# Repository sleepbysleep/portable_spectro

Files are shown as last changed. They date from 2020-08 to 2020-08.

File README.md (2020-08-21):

# Introduction
I just want to make new kind of portable spectrometer, which would be equipped with more-efficient LED illumination ranging from 400nm to 1000nm than Tungsten-Hallogen lamp. The design intends to be switchable between two kinds of miniatured spectrometer(i.e. C12880MA, and ADS8860IDGS) for flexiblity. Indeed, the main controller should handle BlueTooth communication with intermediate device like smart phone or personal computer in order to gather the spectrum data into remote server.

In terms of Vis/NIR radiation, the useful choices are so-called braodband IR LED like SFH4736, SFH4776, and L1IG-0750100000000. Unfortunately, these things doesn't emit visible light except for violet band, which intends to make a phosper excited. So, I have to make the lighting in the combination of Vis LED and such a broadband LEDs. To accomplish proper illumination, many things have to be solved in aspects of blending ratio of Vis, and NIR, and how many LEDs are mounted on PCB for sufficient lighting. Therefore, the below have to be done;

1. Analyze the comparision of spectral intensity among SFH4736, SFH4776, and L1IG-0750100000000.
2. Determine blending ratio of Vis, and NIR LEDs for flatness of spectral intensity from Vis to NIR.
3. Design the hardware that can equip with nRF52840, Vis/NIR LEDs (corresponding driver as well), switchable spectrometer (corresponding periphertal indeed), and power management unit including Li-ion or Li-po battery, charging part, and boost regulator.
4. Develop the firmware that can process the BlueTooth communication with smart phone (iOS, and Android), interfacing the spectrometer, and interactive operation between LED-based illumination, and spectrometer.
5. Develop the application for iOS, and Android that can be portal to pass, and signal process the spectrum into the remote server.
6. Develop the remote server program, that can manage huge spectra with extra infomation (i.e. object, date, dependant like sugar content), and do machine learning, initially being PLS, and SVM-regression hopefully I want to goes into Deap Learning (CNN or RNN).

Definitly, all the staffs are very challenging to me in terms of funding, and workloads. I will do as much as possible!

# Hardware
The hardware consists of Li-ion or Li-po battery, charging unit, boost regulator, C12880MA spectrometer including analog amplifier, and ADC unit, AS7260X spectrometer, and nRF52840 BlueTooth CPU.

TODO: Block diagram

The schematic of ADS8860IDGS is referred from https://www.ti.com/lit/df/tidrau9a/tidrau9a.pdf
TODO: add image with highlight of the copied.

The schematic of C12880MA is referred from https://github.com/Alexey-Danilchenko/Spectron
TODO: add image with highlight of the copied

The schematic of AS7260x is referred from

The schematic of MCP73871 is referred from 

# Mechanical Drawing

# Spectral intesity comparison
TODO: add the graph among them.

# Firmware Design
openocd, my budget is the stlink v2
TODO: add Flow chart
TODO: add block diagram

# Integration time calculation

# App Design

# Server Design

# BOM
Spectrometer: C12880MA, or AS7260x be switchable
CPU: nrf52840, mdbt501-v10
Candidators for Light source: SFH4736, or SFH4776, or L1IG-0750100000000

# References
https://github.com/Alexey-Danilchenko/Spectron

# Appendix

## nRF52840 development environment

Install Toolchain on debian testing(currently bulleseye)
$ apt install libnewlib-dev libstdc++-arm-none-eabi-newlib libnewlib-arm-none-eabi gcc-arm-none-eabi binutils-arm-none-eabi

Verify the version of installed gcc
$ arm-none-eabi-gcc --version
arm-none-eabi-gcc (15:7-2018-q2-6+b1) 7.3.1 20180622 (release) [ARM/embedded-7-branch revision 261907]
Copyright (C) 2017 Free Software Foundation, Inc.
This is free software; see the source for copying conditions.  There is NO
warranty; not even for MERCHANTABILITY or FITNESS FOR A PARTICULAR PURPOSE.

Download, and install the nRF5 SDK
Go to https://www.nordicsemi.com/Software-and-Tools/Software/nRF5-SDK/, and
download the latest verion of SDK at https://www.nordicsemi.com/-/media/Software-and-other-downloads/SDKs/nRF5/Binaries/nRF5_SDK_16.0.0_98a08e2.zip
Unzip nRF5_SDK_16.0.0_98a08e2.zip like as:
nRF5_SDK_16.0.0_98a08e2
+- components
+- config
+- documentation
+- examples
+- external
+- external_tools
+- intergation
+- modules
+- license.txt
+- nRF5x_MDK_8_27_0_IAR_NordicLicense.msi
+- nRF5x_MDK_8_27_0_Keil4_NordicLicense.msi

At "$(SDK_ROOT)/components/toolchain/gcc" under SDK, there are several kinds of Makefile for Windows/Linux/MacOs.
Now, we should edit "Makefile.posix" in the case of Linux or MacOs like the below.

GNU_INSTALL_ROOT ?= /usr/local/gcc-arm-none-eabi-7-2018-q2-update/bin/
GNU_VERSION ?= 7.3.1
GNU_PREFIX ?= arm-none-eabi

into

GNU_INSTALL_ROOT ?= /usr/bin/
GNU_VERSION ?= 7.3.1
GNU_PREFIX ?= arm-none-eabi

Try to compile the example.
Under "$(SDK_ROOT)/examples/peripheral/blinky/PCA10056/blank/armgcc", 
$ make
mkdir _build
cd _build && mkdir nrf52840_xxaa
Assembling file: gcc_startup_nrf52840.S
Compiling file: nrf_log_frontend.c
Compiling file: nrf_log_str_formatter.c
Compiling file: boards.c
Compiling file: app_error.c
Compiling file: app_error_handler_gcc.c
Compiling file: app_error_weak.c
Compiling file: app_util_platform.c
Compiling file: nrf_assert.c
Compiling file: nrf_atomic.c
Compiling file: nrf_balloc.c
Compiling file: nrf_fprintf.c
Compiling file: nrf_fprintf_format.c
Compiling file: nrf_memobj.c
Compiling file: nrf_ringbuf.c
Compiling file: nrf_strerror.c
Compiling file: nrfx_atomic.c
Compiling file: main.c
Compiling file: system_nrf52840.c
Linking target: _build/nrf52840_xxaa.out
   text	   data	    bss	    dec	    hex	filename
   2168	    112	    172	   2452	    994	_build/nrf52840_xxaa.out
Preparing: _build/nrf52840_xxaa.hex
Preparing: _build/nrf52840_xxaa.bin
DONE nrf52840_xxaa

## Install programmer for nRF52, and setup correspondances
Download nRF Command Line Tools via https://www.nordicsemi.com/Software-and-tools/Development-Tools/nRF-Command-Line-Tools/Download#infotabs
In my case of Debian Linux(), the nRF-Command-Line-Tools_10_5_0_Linux-amd64.tar.gz is appropriate.

If you want to generate DFU formatted binary, please see the nRF-Utils for desktop at https://www.nordicsemi.com/Software-and-tools/Development-Tools/nRF-Util. Its actual location is https://github.com/NordicSemiconductor/pc-nrfutil. It isn't dependent from installed OS due to python package.

## Make the new project
Make new directory named as "projects" under the root of SDK.
$ mkdir projects
$ cd projects
$ mkdir template
$ cd ../

Copy files from main.c at examples/peripheral/bliky/, blinky_gcc_nrf52.ld, and Makefile at examples/peripheral/blinky/pca10056/blank/armgcc, and config/sdk_config.h at examples/peripheral/blinky/pca10056/blank into newly created project of projects/template.

$ cp -r ./examples/peripheral/blinky/main.c ./examples/peripheral/blinky/pca10056/blank/armgcc/blinky_gcc_nrf52.ld ./examples/peripheral/blinky/pca10056/blank/armgcc/Makefile ./examples/peripheral/blinky/pca10056/blank/config ./projects/template

Change some definitions in Makefile like;

SDK_ROOT := ../../../../../..
PROJ_DIR := ../../..
...
INC_FOLDERS += \
  $(SDK_ROOT)/components \
  $(SDK_ROOT)/modules/nrfx/mdk \
  $(PROJ_DIR) \
  $(SDK_ROOT)/components/libraries/strerror \
  $(SDK_ROOT)/components/toolchain/cmsis/include \
  $(SDK_ROOT)/components/libraries/util \
  ../config \
...
CFLAGS += -Wall -Werror
as

SDK_ROOT := ../..
PROJ_DIR := .
...
INC_FOLDERS += \
  $(SDK_ROOT)/components \
  $(SDK_ROOT)/modules/nrfx/mdk \
  $(PROJ_DIR) \
  $(SDK_ROOT)/components/libraries/strerror \
  $(SDK_ROOT)/components/toolchain/cmsis/include \
  $(SDK_ROOT)/components/libraries/util \
  ./config \
...
CFLAGS += -Wall #-Werror

Finally, make sure the compilation done.
daysleep@t480s-debian ~/W/p/f/p/template> make
mkdir _build
cd _build && mkdir nrf52840_xxaa
Assembling file: gcc_startup_nrf52840.S
Compiling file: nrf_log_frontend.c
Compiling file: nrf_log_str_formatter.c
Compiling file: boards.c
Compiling file: app_error.c
Compiling file: app_error_handler_gcc.c
Compiling file: app_error_weak.c
Compiling file: app_util_platform.c
Compiling file: nrf_assert.c
Compiling file: nrf_atomic.c
Compiling file: nrf_balloc.c
Compiling file: nrf_fprintf.c
Compiling file: nrf_fprintf_format.c
Compiling file: nrf_memobj.c
Compiling file: nrf_ringbuf.c
Compiling file: nrf_strerror.c
Compiling file: nrfx_atomic.c
Compiling file: main.c
Compiling file: system_nrf52840.c
Linking target: _build/nrf52840_xxaa.out
   text	   data	    bss	    dec	    hex	filename
   2168	    112	    172	   2452	    994	_build/nrf52840_xxaa.out
Preparing: _build/nrf52840_xxaa.hex
Preparing: _build/nrf52840_xxaa.bin
DONE nrf52840_xxaa

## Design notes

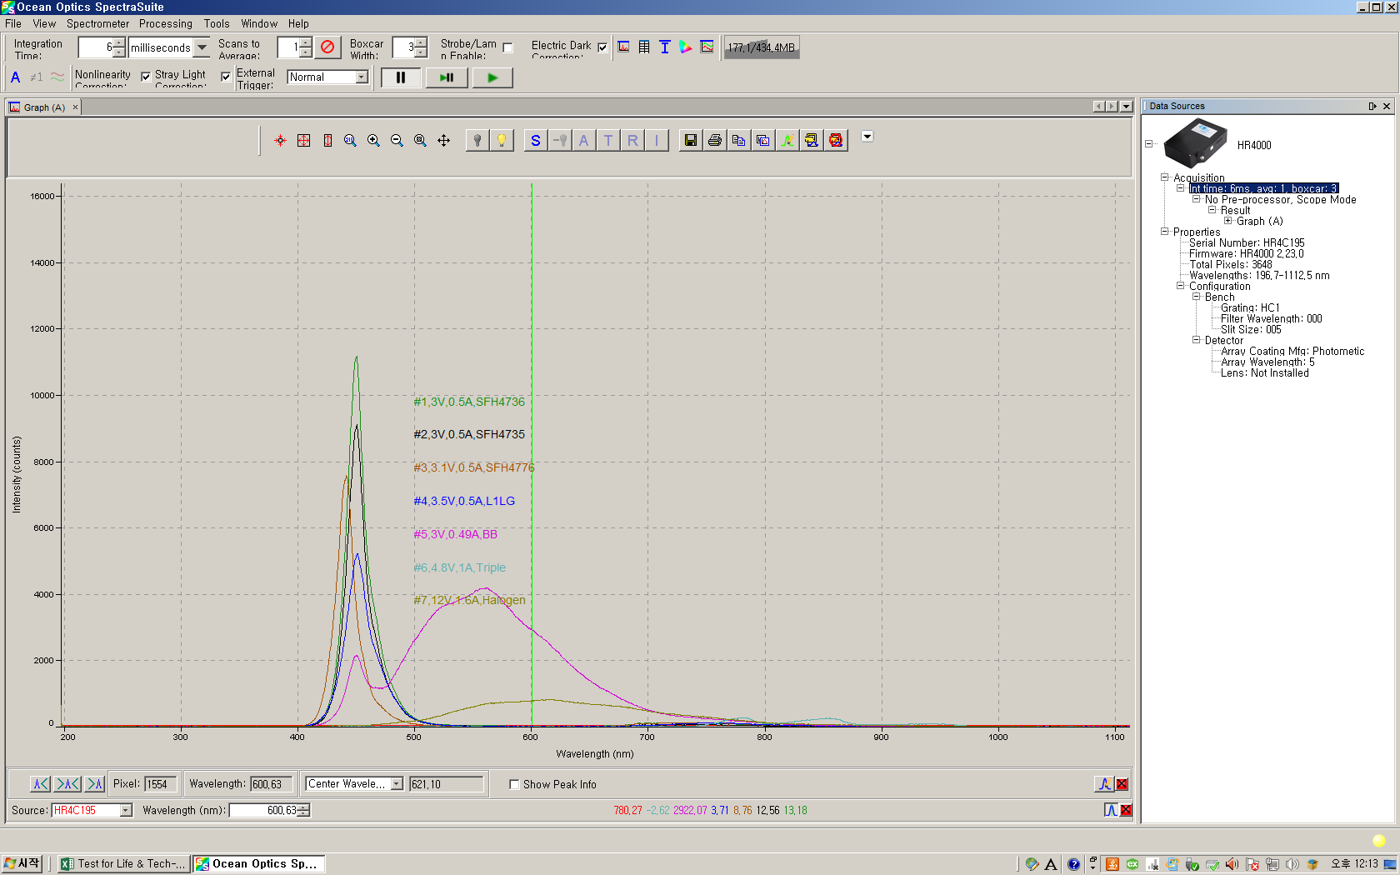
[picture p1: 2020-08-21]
spectral_comparison.png

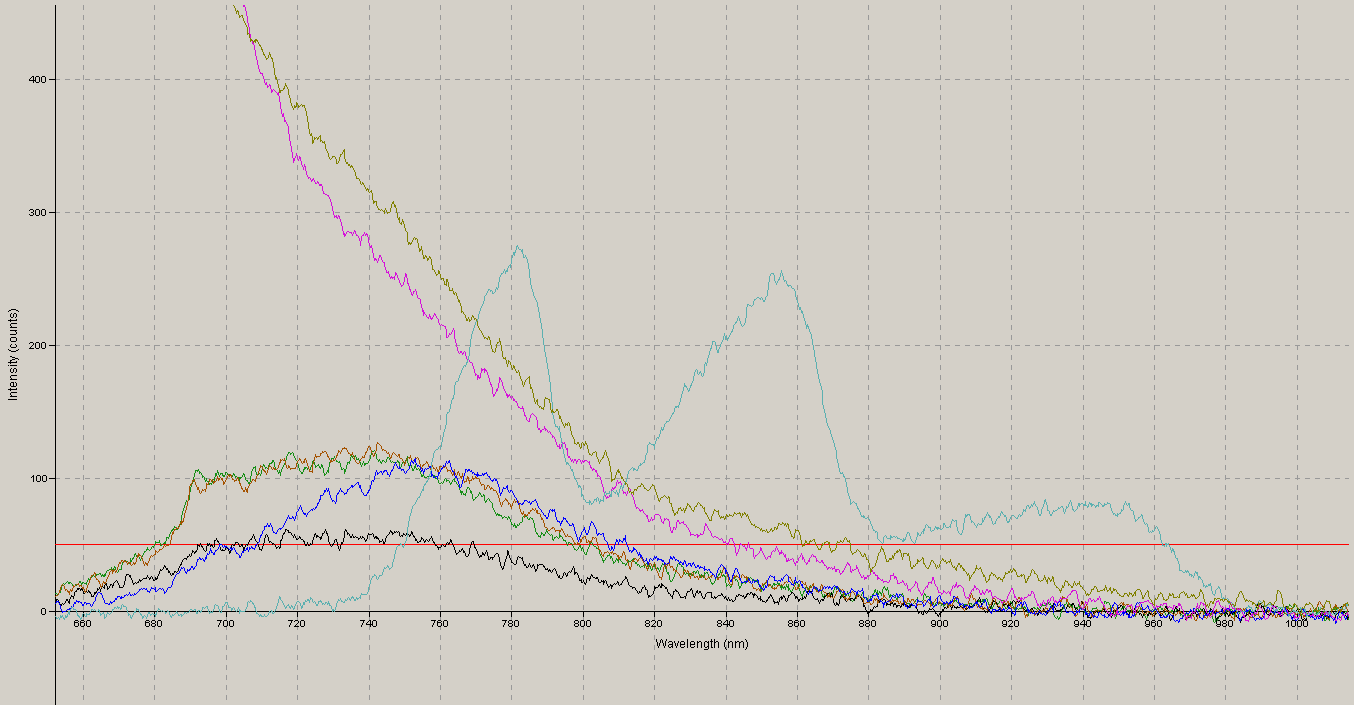
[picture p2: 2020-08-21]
spectral_comparison_zoomin_2.png

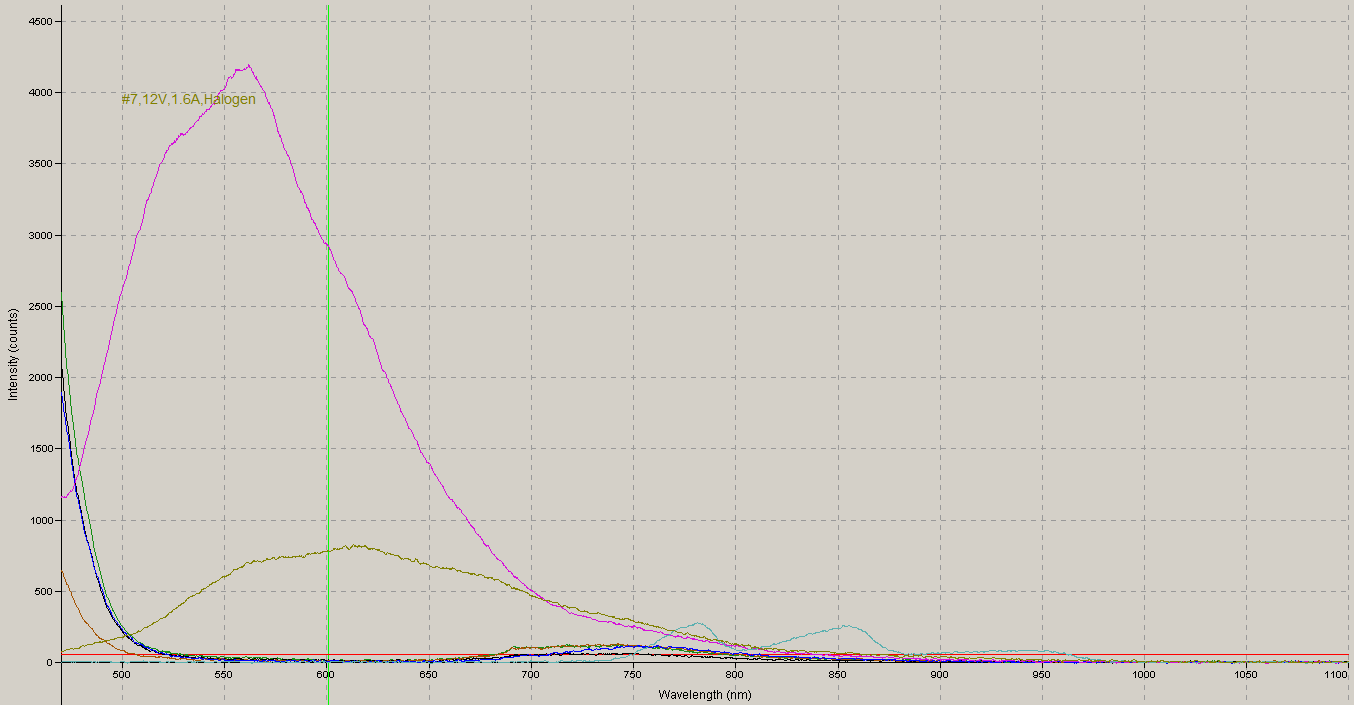
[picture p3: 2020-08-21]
spectral_comparison_zoomin_1.png

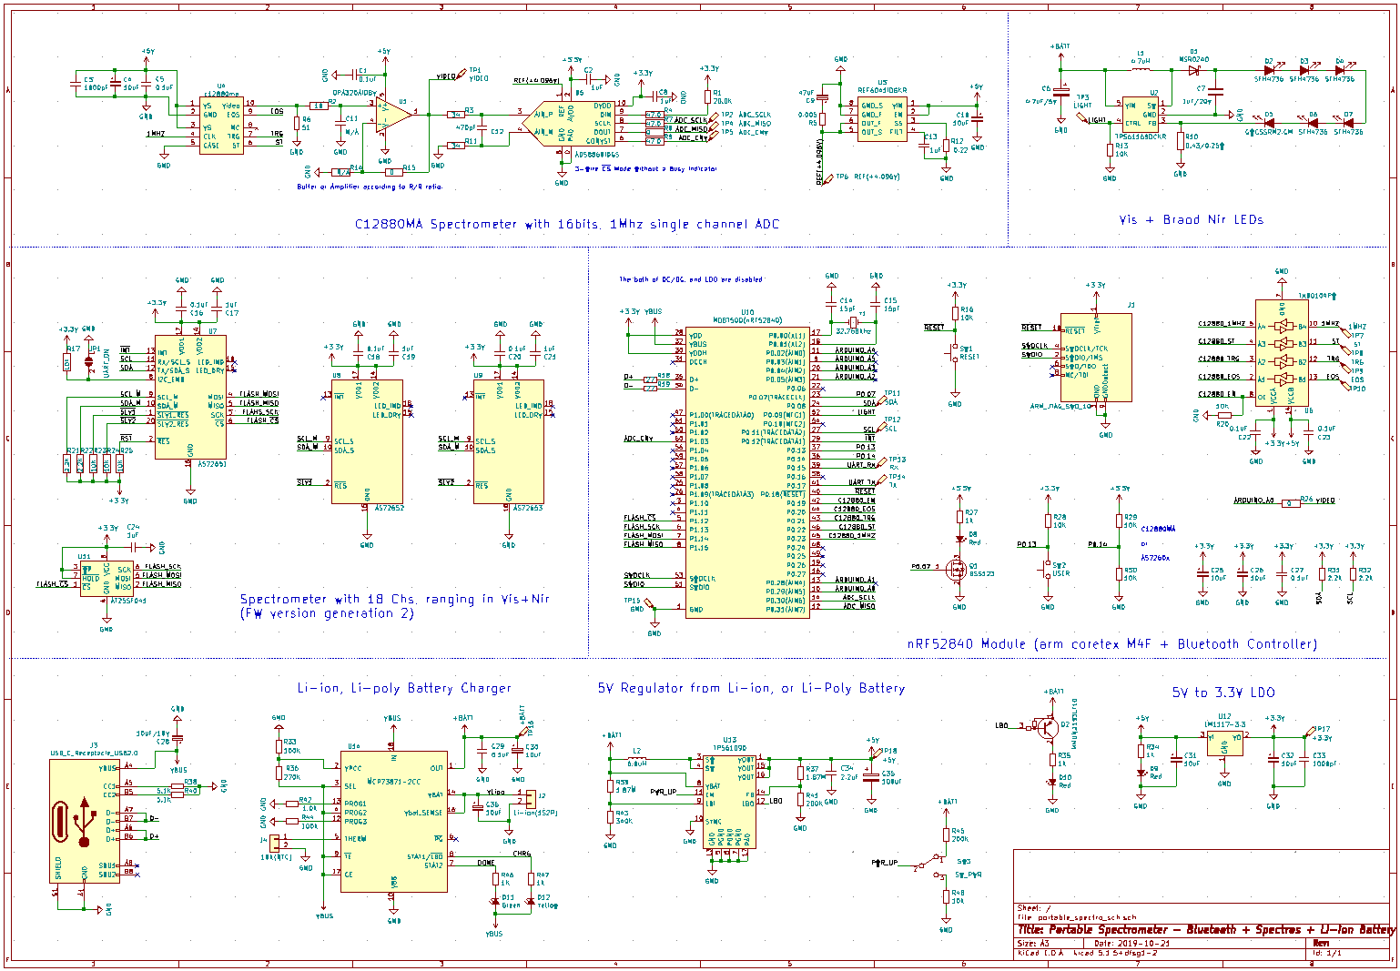
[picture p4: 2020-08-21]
hardware/portable_spectro_sch/Screenshot_2020-01-17_14-10-35.png

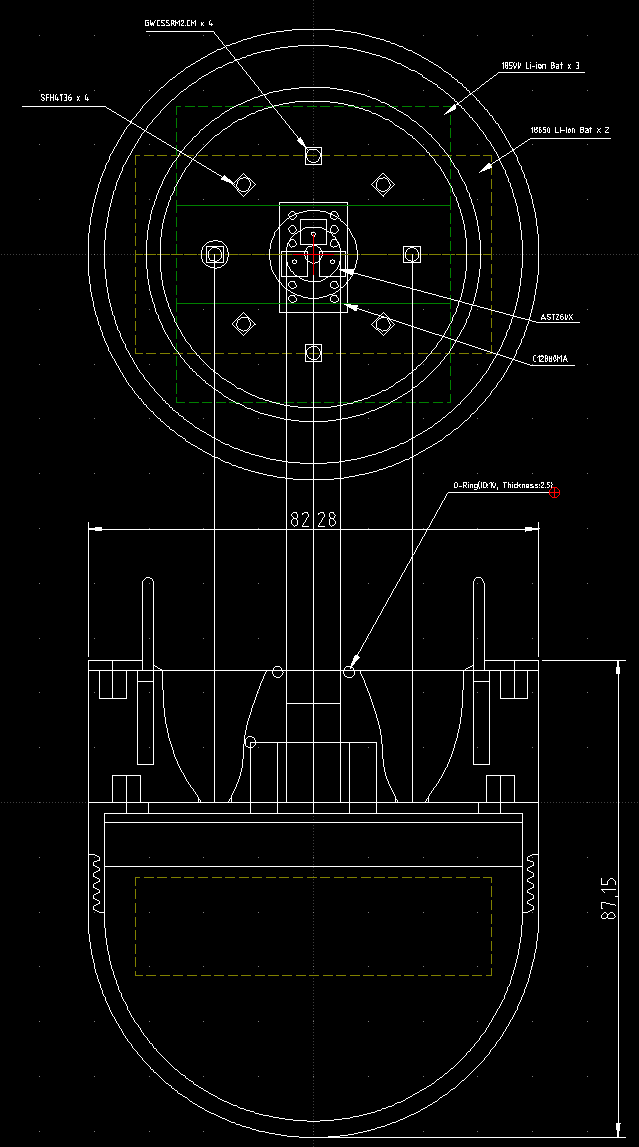
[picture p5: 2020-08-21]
hardware/Screenshot_2020-06-12_15-41-57.png

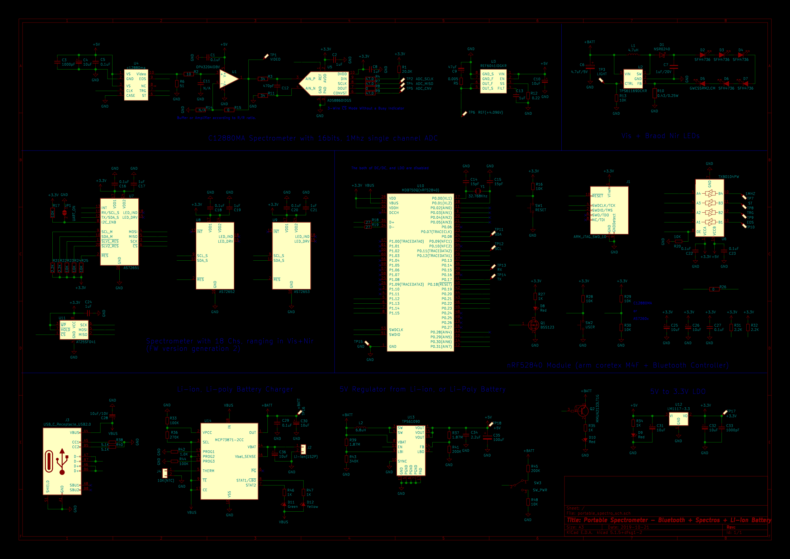
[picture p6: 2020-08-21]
hardware/portable_spectro_sch/portable_spectro_sch.png

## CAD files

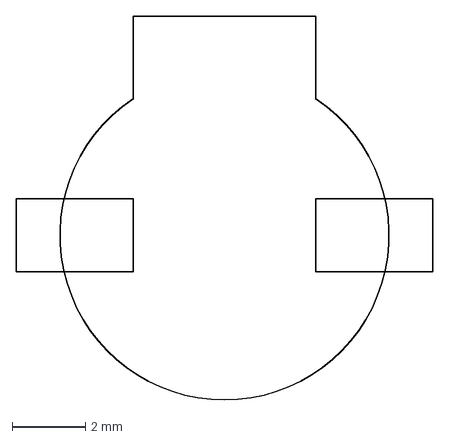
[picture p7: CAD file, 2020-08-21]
hardware/CMT-0926-86-SMT-TR.dxf
11.4 x 10.5 mm

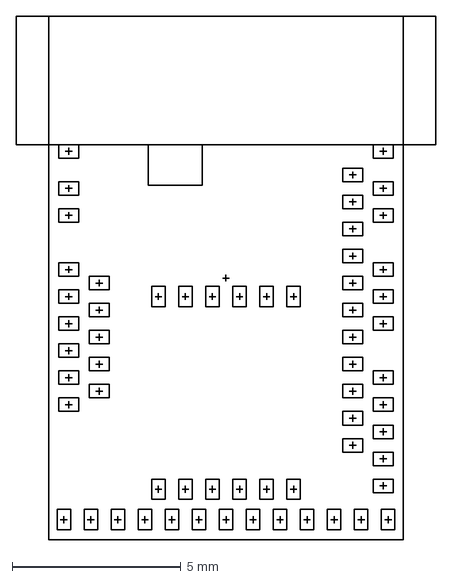
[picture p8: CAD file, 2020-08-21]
hardware/MDBT50Q.dxf
12.4 x 15.5 mm

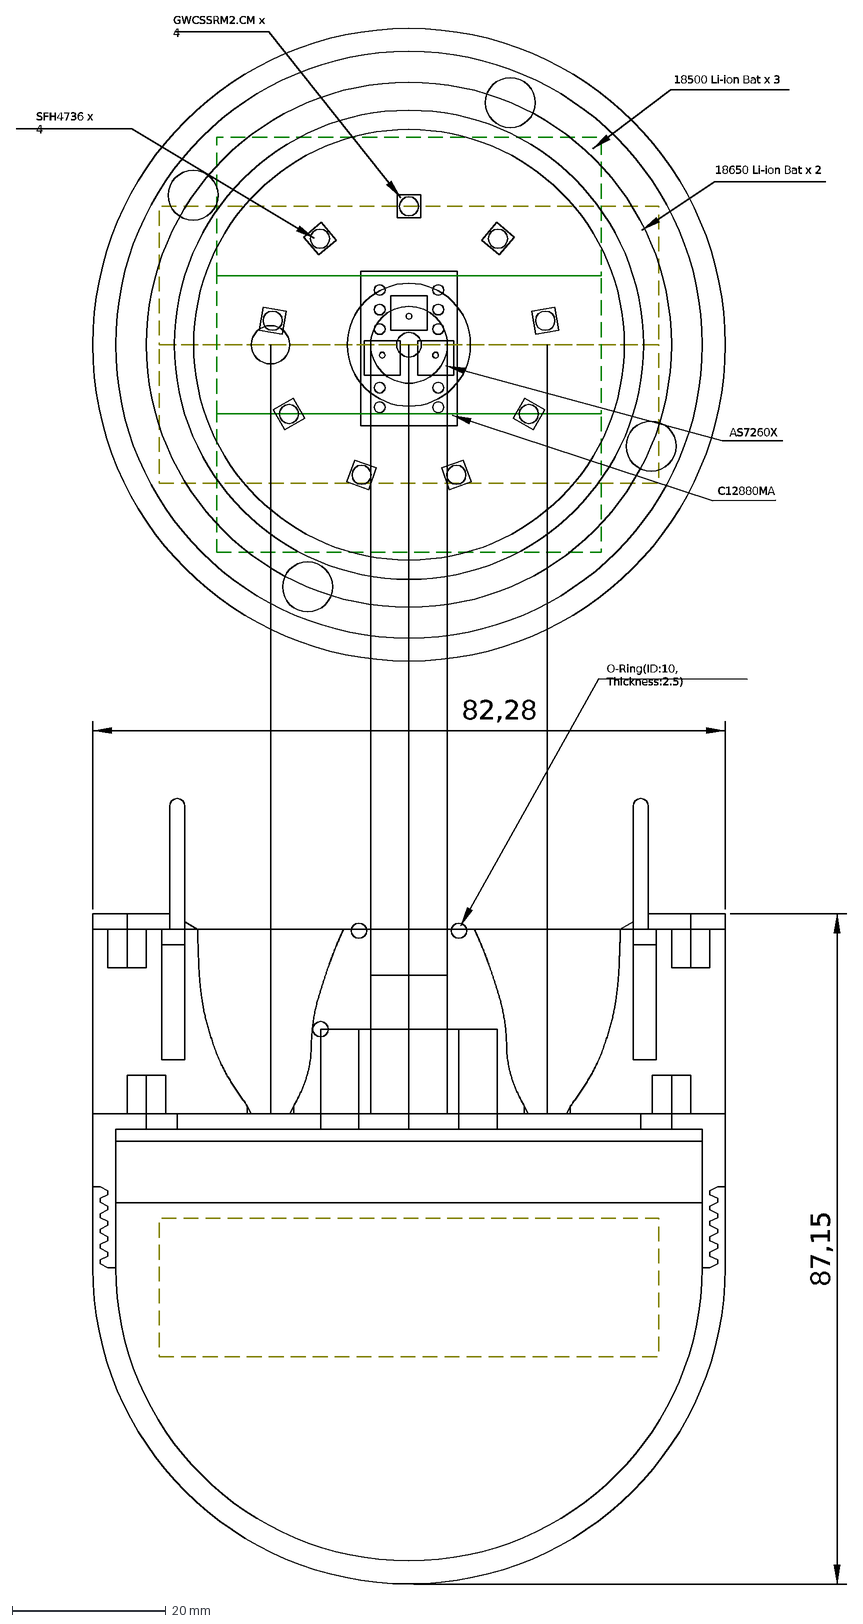
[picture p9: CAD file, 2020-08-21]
hardware/portable_spectro_drawing/portable_spectro_v0.0.1.dxf
18650 Li-ion Bat x 2
18500 Li-ion Bat x 3
C12880MA
AS7260X
GWCSSRM2.CM x 4
87,15
O-Ring(ID:10, Thickness:2.5)
82,28
SFH4736 x 4

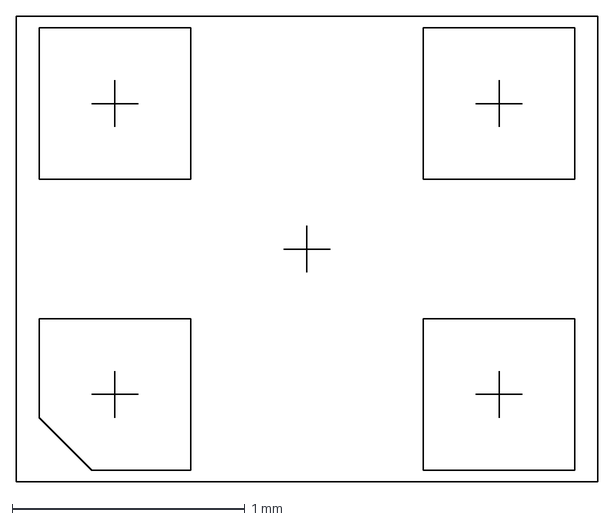
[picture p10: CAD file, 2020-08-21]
hardware/DSC6183JI2A-032K768.dxf
2.50 x 2.00 mm

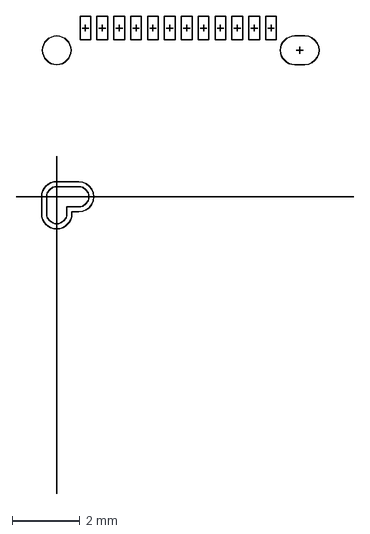
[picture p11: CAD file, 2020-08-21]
hardware/usb_c_receptacle(UJ31-CH-3-SMT-TR).dxf
10.00 x 14.1 mm

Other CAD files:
hardware/portable_spectro_drawing/portable_spectro_draft.dxf

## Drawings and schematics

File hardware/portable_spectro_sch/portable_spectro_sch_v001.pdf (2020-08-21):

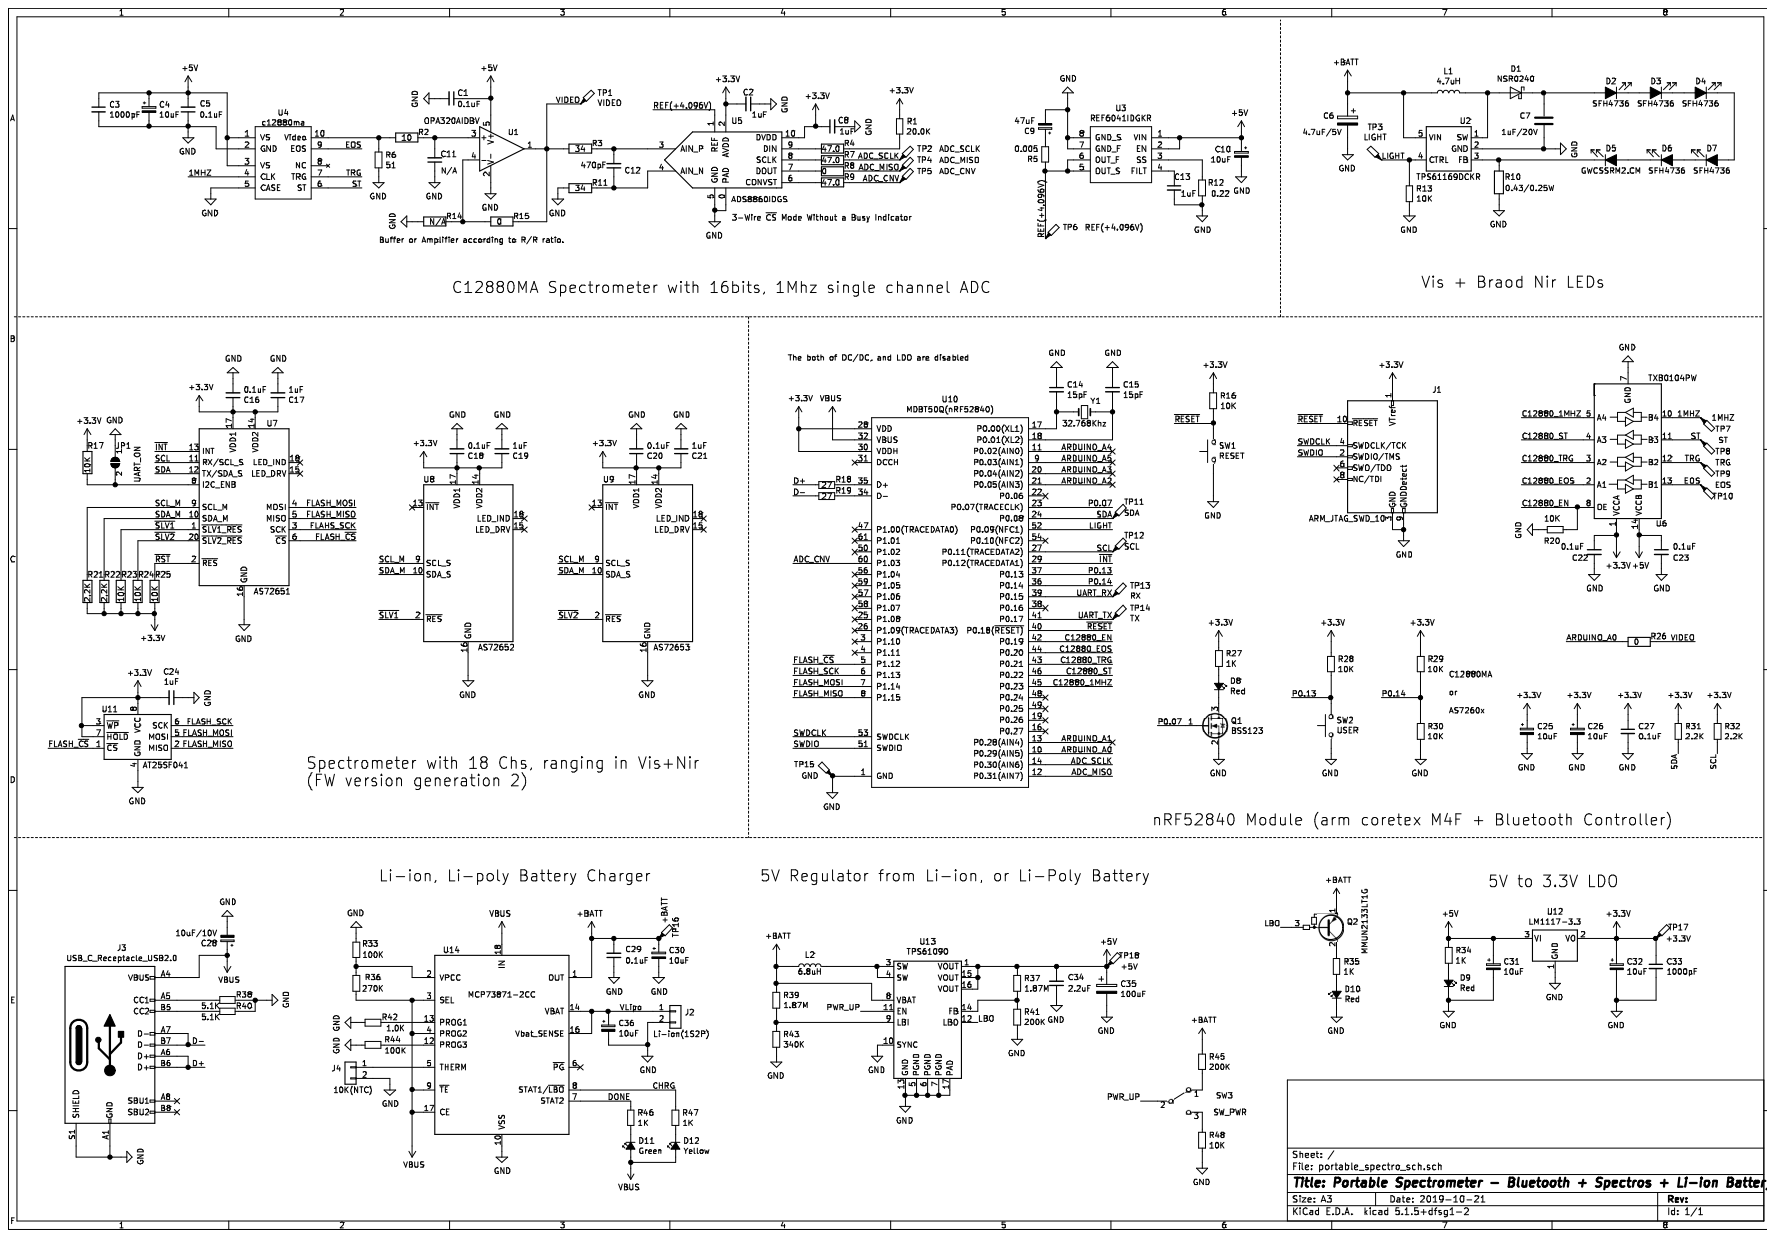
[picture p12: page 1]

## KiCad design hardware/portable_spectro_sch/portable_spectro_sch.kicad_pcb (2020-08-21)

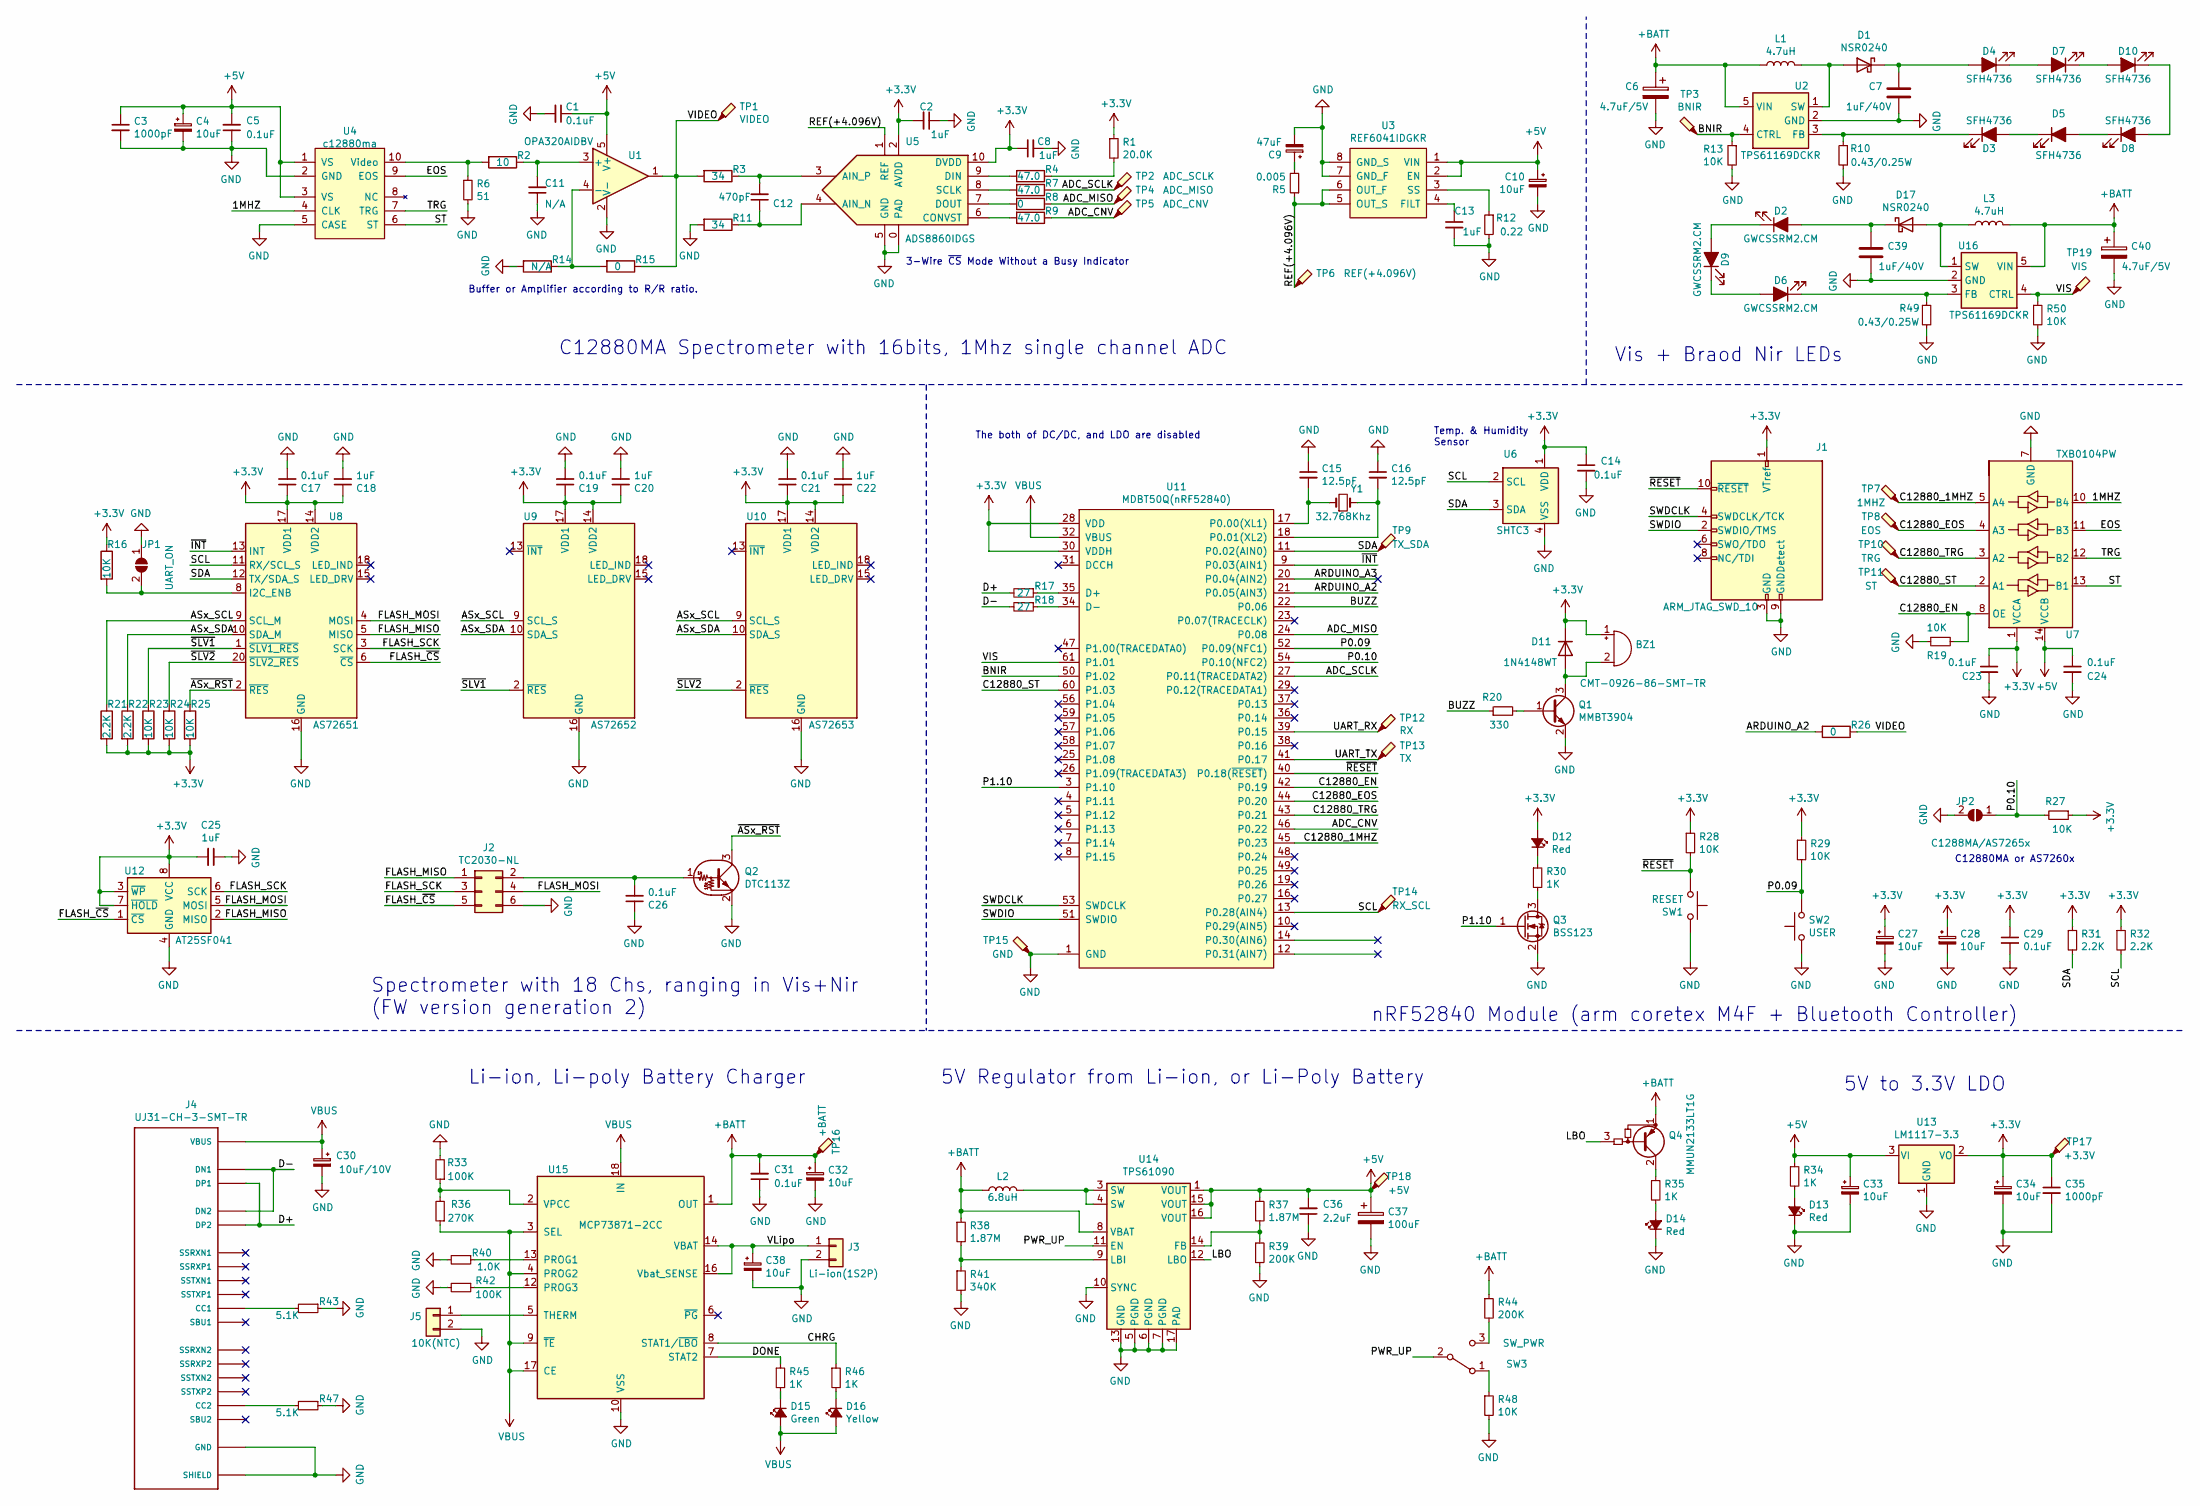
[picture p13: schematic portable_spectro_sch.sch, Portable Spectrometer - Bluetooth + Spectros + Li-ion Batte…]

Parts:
BZ1: CMT-0926-86-SMT-TR; Buzzer_CUI_CMT-0926-86-SMT-TR
C1, C5, C14, C17, C19, C21, C23, C24, C26, C29, C31: 0.1uF; C_0805_2012Metric
C2, C8, C13, C18, C20, C22, C25: 1uF; C_0805_2012Metric
C3, C35: 1000pF; C_0805_2012Metric
C4, C10, C27, C28, C32, C33, C38: 10uF; C_1206_3216Metric
C6, C40: 4.7uF/5V; C_1206_3216Metric
C7, C39: 1uF/40V; C_0805_2012Metric
C9: 47uF; CP_Elec_5x5.4
C11: N/A; C_0805_2012Metric
C12: 470pF; C_0805_2012Metric
C15, C16: 12.5pF; C_0805_2012Metric
C30: 10uF/10V; C_1206_3216Metric
C34: 10uF; CP_Elec_5x5.4
C36: 2.2uF; C_0805_2012Metric
C37: 100uF; CP_Elec_6.3x5.4
D1, D17: NSR0240; D_SOD-323
D2, D6, D9: GWCSSRM2.CM; LED-GWCSSRM2.CM_OSRAM-thermalvia
D3, D4, D5, D7, D8, D10: SFH4736; LED-GWCSSRM2.CM_OSRAM-thermalvia
D11: 1N4148WT; D_SOD-523
D12, D13, D14: Red; D_0805_2012Metric
D15: Green; D_0805_2012Metric
D16: Yellow; D_0805_2012Metric
J1: ARM_JTAG_SWD_10; PinHeader_2x05_P1.27mm_Vertical
J2: TC2030-NL; Tag-Connect_TC2030-IDC-NL_2x03_P1.27mm_Vertical
J3: Li-ion(1S2P); JST_PH_B2B-PH-K_1x02_P2.00mm_Vertical
J4: UJ31-CH-3-SMT-TR; CUI_UJ31-CH-3-SMT-TR
J5: 10K(NTC); PinHeader_1x02_P1.27mm_Vertical
JP1: UART_ON; SolderJumper-2_P1.3mm_Open_RoundedPad1.0x1.5mm
JP2: C1288MA/AS7265x; SolderJumper-2_P1.3mm_Open_RoundedPad1.0x1.5mm
L1, L3: 4.7uH; L_Laird_TYS4030150M-10
L2: 6.8uH; L_Laird_TYS5040470M-10
Q1: MMBT3904; SOT-23
Q2: DTC113Z; SOT-23
Q3: BSS123; SOT-23
Q4: MMUN2133LT1G; SOT-23
R1: 20.0K; R_0805_2012Metric
R2: 10; R_0805_2012Metric
R3, R11: 34; R_0805_2012Metric
R4, R7, R9: 47.0; R_0805_2012Metric
R5: 0.005; R_0805_2012Metric
R6: 51; R_0805_2012Metric
R8, R15, R26: 0; R_0805_2012Metric
R10, R49: 0.43/0.25W; R_1206_3216Metric
R12: 0.22; R_0805_2012Metric
R13, R16, R19, R23, R24, R25, R27, R28, R29, R48, R50: 10K; R_0805_2012Metric
R14: N/A; R_0805_2012Metric
R17, R18: 27; R_0805_2012Metric
R20: 330; R_0805_2012Metric
R21, R22, R31, R32: 2.2K; R_0805_2012Metric
R30, R34, R35, R45, R46: 1K; R_0805_2012Metric
R33, R42: 100K; R_0805_2012Metric
R36: 270K; R_0805_2012Metric
R37, R38: 1.87M; R_0805_2012Metric
R39, R44: 200K; R_0805_2012Metric
R40: 1.0K; R_0805_2012Metric
R41: 340K; R_0805_2012Metric
R43, R47: 5.1K; R_0805_2012Metric
SW1: RESET; SW_Tactile_SPST_Angled_PTS645Vx39-2LFS
SW2: USER; SW_Tactile_SPST_Angled_PTS645Vx39-2LFS
SW3: SW_PWR; SW_E-Switch_EG1206_SPDT_Angled
TP1: VIDEO; TestPoint_Pad_D1.0mm
TP2: ADC_SCLK; TestPoint_Pad_D1.0mm
TP3: BNIR; TestPoint_Pad_D1.0mm
TP4: ADC_MISO; TestPoint_Pad_D1.0mm
TP5: ADC_CNV; TestPoint_Pad_D1.0mm
TP6: REF(+4.096V); TestPoint_Pad_D1.0mm
TP7: 1MHZ; TestPoint_Pad_D1.0mm
TP8: EOS; TestPoint_Pad_D1.0mm
TP9: TX_SDA; TestPoint_Pad_D1.0mm
TP10: TRG; TestPoint_Pad_D1.0mm
TP11: ST; TestPoint_Pad_D1.0mm
TP12: RX; TestPoint_Pad_D1.0mm
TP13: TX; TestPoint_Pad_D1.0mm
TP14: RX_SCL; TestPoint_Pad_D1.0mm
TP15: GND; TestPoint_Pad_D1.0mm
TP16: +BATT; TestPoint_Pad_D1.0mm
TP17: +3.3V; TestPoint_Pad_D1.0mm
TP18: +5V; TestPoint_Pad_D1.0mm
TP19: VIS; TestPoint_Pad_D1.0mm
U1: OPA320AIDBV; SOT-23-5
U2, U16: TPS61169DCKR; SOT-353_SC-70-5
U3: REF6041IDGKR; VSSOP-8_3.0x3.0mm_P0.65mm
U4: c12880ma; C12880MA
U5: ADS8860IDGS; VSSOP-10_3x3mm_P0.5mm
U6: SHTC3; Sensirion_DFN-4-1EP_2x2mm_P1mm_EP0.7x1.6mm
U7: TXB0104PW; TSSOP-14_4.4x5mm_P0.65mm
U8: AS72651; AS7265x_LGA-20_4.6x4.4_Pitch0.65mm
U9: AS72652; AS7265x_LGA-20_4.6x4.4_Pitch0.65mm
U10: AS72653; AS7265x_LGA-20_4.6x4.4_Pitch0.65mm
U11: MDBT50Q(nRF52840); MDBT50Q-nRF52840
U12: AT25SF041; SOIC-8_3.9x4.9mm_P1.27mm
U13: LM1117-3.3; SOT-223-3_TabPin2
U14: TPS61090; Texas_S-PVQFN-N16_EP2.7x2.7mm_ThermalVias
U15: MCP73871-2CC; QFN-20-1EP_4x4mm_P0.5mm_EP2.5x2.5mm
Y1: 32.768Khz; Crystal_SMD_Epson_FC-135-2Pin_3.2x2.5mm

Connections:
+3V3: BZ1.1 (-), C2.2, C8.1, C14.1, C17.1, C18.1, C19.1, C20.1, C21.1, C22.1, C23.1, C25.2, C27.1, C28.1, C29.1, C34.1, C35.1, D11.1 (K), D12.2 (A), J1.1 (VTref), R1.1, R16.1, R21.2, R22.2, R23.2, R24.2, R25.2, R27.1, R28.1, R29.1, R31.1, R32.1, TP17.1, U5.2 (AVDD), U5.10 (DVDD), U6.1 (VDD), U7.1 (VCCA), U8.14 (VDD2), U8.17 (VDD1), U9.14 (VDD2), U9.17 (VDD1), U10.14 (VDD2), U10.17 (VDD1), U11.28 (VDD), U11.30 (VDDH), U12.3 (~WP), U12.7 (~HOLD), U12.8 (VCC), U13.2 (VO)
+5V: C1.1, C3.1, C4.1, C5.2, C10.1, C24.1, C33.1, C36.2, C37.1, R34.1, R37.1, TP18.1, U1.5 (V+), U3.1 (VIN), U3.2 (EN), U4.1 (VS), U4.3 (VS), U7.14 (VCCB), U13.3 (VI), U14.1 (VOUT), U14.15 (VOUT), U14.16 (VOUT)
+BATT: C6.1, C31.2, C32.1, C40.1, L1.2, L2.1, L3.2, Q4.1 (E), R38.1, R44.1, TP16.1, U2.5 (VIN), U14.8 (VBAT), U15.1 (OUT), U15.20 (OUT), U16.5 (VIN)
/1MHZ: U4.4 (CLK), U7.10 (B4)
/ADC_CNV: R9.1, TP5.1, U11.46 (P0.22)
/ADC_MISO: R8.1, TP4.1, U11.24 (P0.08)
/ADC_SCLK: R7.1, TP2.1, U11.27 (P0.11(TRACEDATA2))
/ARDUINO_A2: R26.2, U11.21 (P0.05(AIN3))
/ARDUINO_A3: U11.20 (P0.04(AIN2))
/ASx_SCL: R21.1, U8.9 (SCL_M), U9.9 (SCL_S), U10.9 (SCL_S)
/ASx_SDA: R22.1, U8.10 (SDA_M), U9.10 (SDA_S), U10.10 (SDA_S)
/BNIR: R13.1, TP3.1, U2.4 (CTRL), U11.50 (P1.02)
/BUZZ: R20.1, U11.22 (P0.06)
/C12880_1MHZ: TP7.1, U7.5 (A4), U11.45 (P0.23)
/C12880_EN: R19.2, U7.8 (OE), U11.42 (P0.19)
/C12880_EOS: TP8.1, U7.4 (A3), U11.44 (P0.20)
/C12880_ST: TP11.1, U7.2 (A1), U11.60 (P1.03)
/C12880_TRG: TP10.1, U7.3 (A2), U11.43 (P0.21)
/CHRG: R46.1, U15.8 (STAT1/~LBO~)
/D+: J4.A6 (DP1), J4.B6 (DP2), R17.2
/D-: J4.A7 (DN1), J4.B7 (DN2), R18.2
/DONE: R45.1, U15.7 (STAT2)
/EOS: U4.9 (EOS), U7.11 (B3)
/FLASH_MISO: J2.1, U8.5 (MISO), U12.2 (MISO)
/FLASH_MOSI: J2.4, U8.4 (MOSI), U12.5 (MOSI)
/FLASH_SCK: J2.3, U8.3 (SCK), U12.6 (SCK)
/FLASH_~CS: J2.5, U8.6 (~CS), U12.1 (~CS)
/LBO: Q4.3 (B), U14.12 (LBO)
/P0.09: R29.2, SW2.2, U11.52 (P0.09(NFC1))
/P0.10: JP2.1 (A), R27.2, U11.54 (P0.10(NFC2))
/P1.10: Q3.1 (G), U11.3 (P1.10)
/PWR_UP: SW3.2 (B), U14.11 (EN)
/REF(+4.096V): R5.1, TP6.1, U3.5 (OUT_S), U3.6 (OUT_F), U5.1 (REF)
/SCL: R32.2, TP14.1, U6.2 (SCL), U8.11 (RX/SCL_S), U11.13 (P0.28(AIN4))
/SDA: R31.2, TP9.1, U6.3 (SDA), U8.12 (TX/SDA_S), U11.11 (P0.02(AIN0))
/ST: U4.6 (ST), U7.13 (B1)
/SWDCLK: J1.4 (SWDCLK/TCK), U11.53 (SWDCLK)
/SWDIO: J1.2 (SWDIO/TMS), U11.51 (SWDIO)
/TRG: U4.7 (TRG), U7.12 (B2)
/UART_RX: TP12.1, U11.39 (P0.15)
/UART_TX: TP13.1, U11.41 (P0.17)
/VIDEO: R3.2, R15.1, R26.1, TP1.1, U1.1
/VIS: R50.1, TP19.1, U11.61 (P1.01), U16.4 (CTRL)
/VLipo: C38.1, J3.1, U15.14 (VBAT), U15.15 (VBAT), U15.16 (Vbat_SENSE)
/~ASx_RST: Q2.3 (C), R25.1, U8.2 (~RES)
/~INT: U8.13 (INT), U11.9 (P0.03(AIN1))
/~RESET: J1.10 (~RESET~), R28.2, SW1.1, U11.40 (P0.18(~RESET))
/~SLV1: R23.1, U8.1 (~SLV1_RES), U9.2 (~RES)
/~SLV2: R24.1, U8.20 (~SLV2_RES), U10.2 (~RES)
GND: C1.2, C2.1, C3.2, C4.2, C5.1, C6.2, C7.2, C8.2, C9.2, C10.2, C11.1, C13.2, C14.2, C15.1, C16.1, C17.2, C18.2, C19.2, C20.2, C21.2, C22.2, C23.2, C24.2, C25.1, C26.1, C27.2, C28.2, C29.2, C30.2, C31.1, C32.2, C33.2, C34.2, C35.2, C36.1, C37.2, C38.2, C39.2, C40.2, D13.1 (K), D14.1 (K), J1.3 (GND), J1.5 (GND), J1.9 (GNDDetect), J2.6, J3.2, J4.A1 (GND), J4.A12 (GND), J4.B1 (GND), J4.B12 (GND), J4.SH1 (SHIELD), J4.SH2 (SHIELD), J4.SH3 (SHIELD), J4.SH4 (SHIELD), J4.SH5 (SHIELD), J4.SH6 (SHIELD), J5.2, JP1.1 (A), JP2.2 (B), Q1.2 (E), Q2.2 (E), Q3.2 (S), R6.2, R10.2, R11.2, R12.2, R13.2, R14.2, R19.1, R33.2, R39.2, R40.2, R41.2, R42.2, R43.1, R47.1, R48.2, R49.2, R50.2, SW1.2, SW2.1, TP15.1, U1.2 (V-), U2.2 (GND), U3.7 (GND_F), U3.8 (GND_S), U4.2 (GND), U4.5 (CASE), U5.0 (PAD), U5.5 (GND), U6.4 (VSS), U7.7 (GND), U8.16 (GND), U9.16 (GND), U10.16 (GND), U11.1 (GND), U11.2 (GND), U11.15 (GND), U11.33 (GND), U11.55 (GND), U12.4 (GND), U13.1 (GND), U14.5 (PGND), U14.6 (PGND), U14.7 (PGND), U14.10 (SYNC), U14.13 (GND), U14.17 (PAD), U15.10 (VSS), U15.11 (VSS), U15.21 (VSS), U16.2 (GND)
unnamed: BZ1.2 (+), D11.2 (A), Q1.3 (C)
unnamed: C7.1, D1.1 (K), D4.2 (A)
unnamed: C9.1, R5.2
unnamed: C11.2, R2.1, U1.3 (+)
unnamed: C12.1, R11.1, U5.4 (AIN_N)
unnamed: C12.2, R3.1, U5.3 (AIN_P)
unnamed: C13.1, U3.4 (FILT)
unnamed: C15.2, U11.17 (P0.00(XL1)), Y1.1
unnamed: C16.2, U11.18 (P0.01(XL2)), Y1.2
unnamed: C26.2, J2.2, Q2.1 (B)
unnamed: C39.1, D2.2 (A), D17.1 (K)
unnamed: D1.2 (A), L1.1, U2.1 (SW)
unnamed: D2.1 (K), D9.2 (A)
unnamed: D3.1 (K), R10.1, U2.3 (FB)
unnamed: D3.2 (A), D5.1 (K)
unnamed: D4.1 (K), D7.2 (A)
unnamed: D5.2 (A), D8.1 (K)
unnamed: D6.1 (K), R49.1, U16.3 (FB)
unnamed: D6.2 (A), D9.1 (K)
unnamed: D8.2 (A), D10.1 (K)
unnamed: D7.1 (K), D10.2 (A)
unnamed: D12.1 (K), R30.1
unnamed: D13.2 (A), R34.2
unnamed: D14.2 (A), R35.2
unnamed: D15.1 (K), R45.2
unnamed: D16.1 (K), R46.2
unnamed: D17.2 (A), L3.1, U16.1 (SW)
unnamed: J4.A5 (CC1), R43.2
unnamed: J4.B5 (CC2), R47.2
unnamed: J5.1, U15.5 (THERM)
unnamed: JP1.2 (B), R16.2, U8.8 (I2C_ENB)
unnamed: L2.2, U14.3 (SW), U14.4 (SW)
unnamed: Q1.1 (B), R20.2
unnamed: Q3.3 (D), R30.2
unnamed: Q4.2 (C), R35.1
unnamed: R1.2, R4.1
unnamed: R2.2, R6.1, U4.10 (Video)
unnamed: R4.2, U5.9 (DIN)
unnamed: R7.2, U5.8 (SCLK)
unnamed: R8.2, U5.7 (DOUT)
unnamed: R9.2, U5.6 (CONVST)
unnamed: R12.1, U3.3 (SS)
unnamed: R14.1, R15.2, U1.4 (-)
unnamed: R17.1, U11.35 (D+)
unnamed: R18.1, U11.34 (D-)
unnamed: R33.1, R36.2, U15.2 (VPCC)
unnamed: R37.2, R39.1, U14.14 (FB)
unnamed: R38.2, R41.1, U14.9 (LBI)
unnamed: R40.1, U15.13 (PROG1)
unnamed: R42.1, U15.12 (PROG3)
unnamed: R44.2, SW3.3 (C)
unnamed: R48.1, SW3.1 (A)
VBUS: C30.1, D15.2 (A), D16.2 (A), J4.A4 (VBUS), J4.A9 (VBUS), J4.B4 (VBUS), J4.B9 (VBUS), R36.1, U11.32 (VBUS), U15.3 (SEL), U15.4 (PROG2), U15.9 (~TE), U15.17 (CE), U15.18 (IN), U15.19 (IN)

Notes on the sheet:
C12880MA Spectrometer with 16bits, 1Mhz single channel ADC
Spectrometer with 18 Chs, ranging in Vis+Nir (FW version generation 2)
nRF52840 Module (arm coretex M4F + Bluetooth Controller)
The both of DC/DC, and LDO are disabled
C12880MA or AS7260x
Vis + Braod Nir LEDs
5V to 3.3V LDO
5V Regulator from Li-ion, or Li-Poly Battery
Li-ion, Li-poly Battery Charger
3-Wire ~CS~ Mode Without a Busy Indicator
Buffer or Amplifier according to R/R ratio.
Temp. & Humidity Sensor

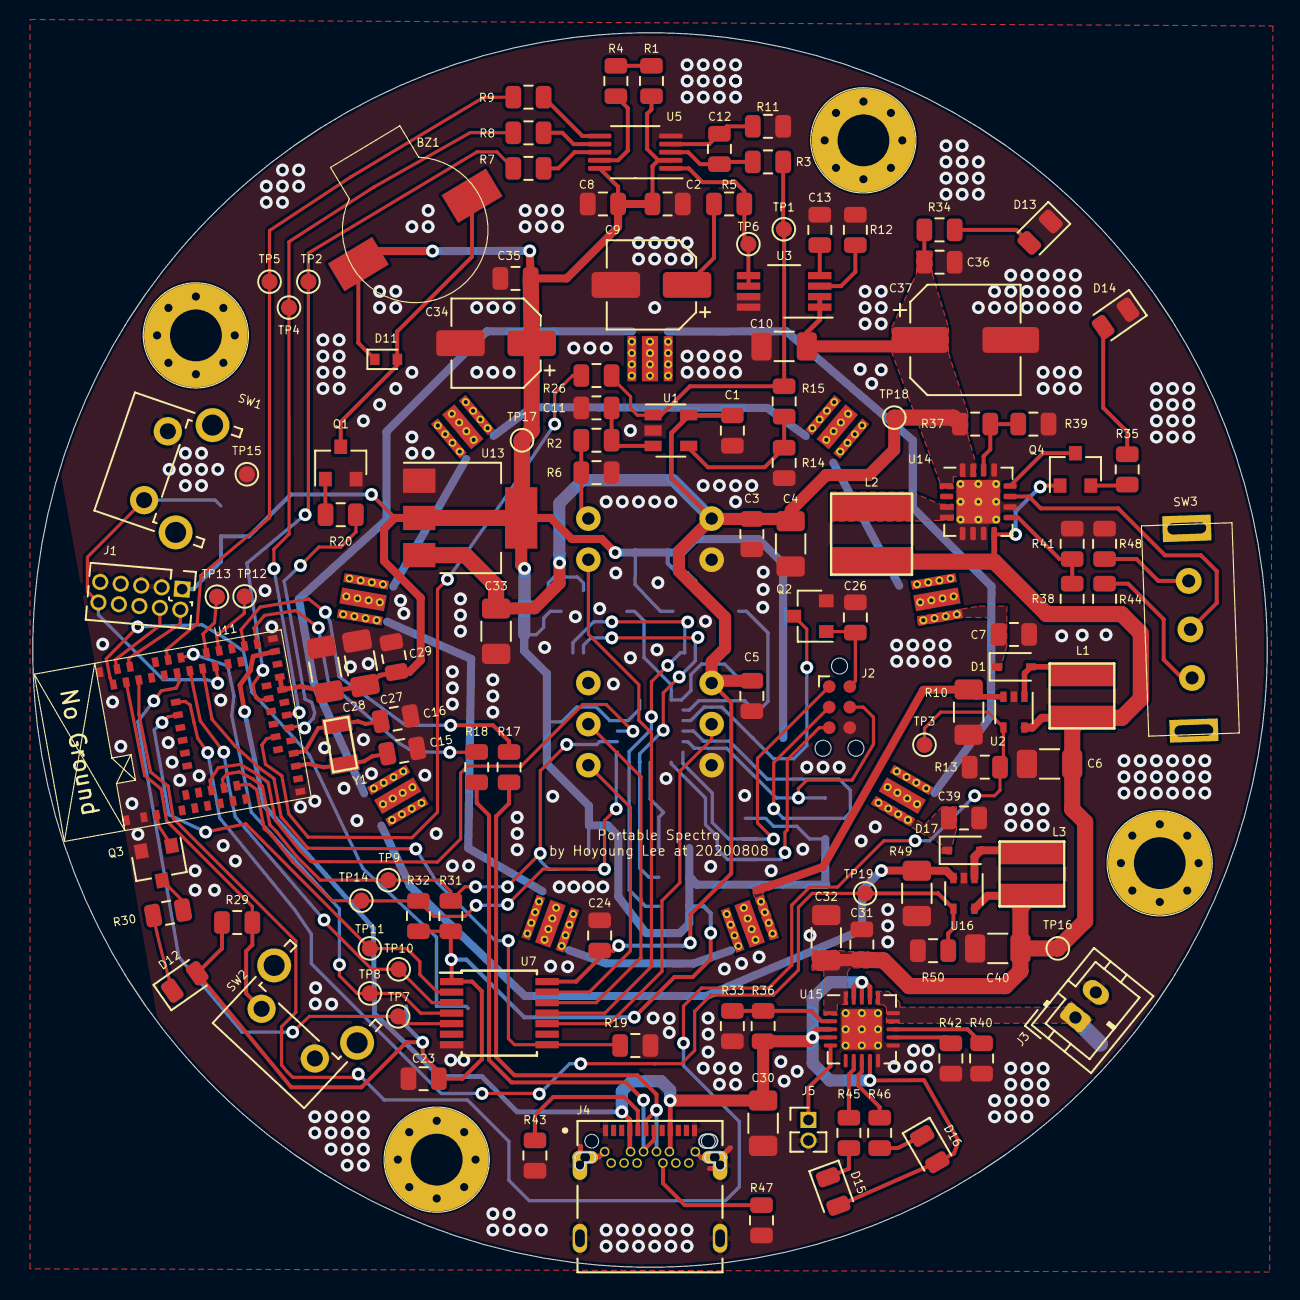
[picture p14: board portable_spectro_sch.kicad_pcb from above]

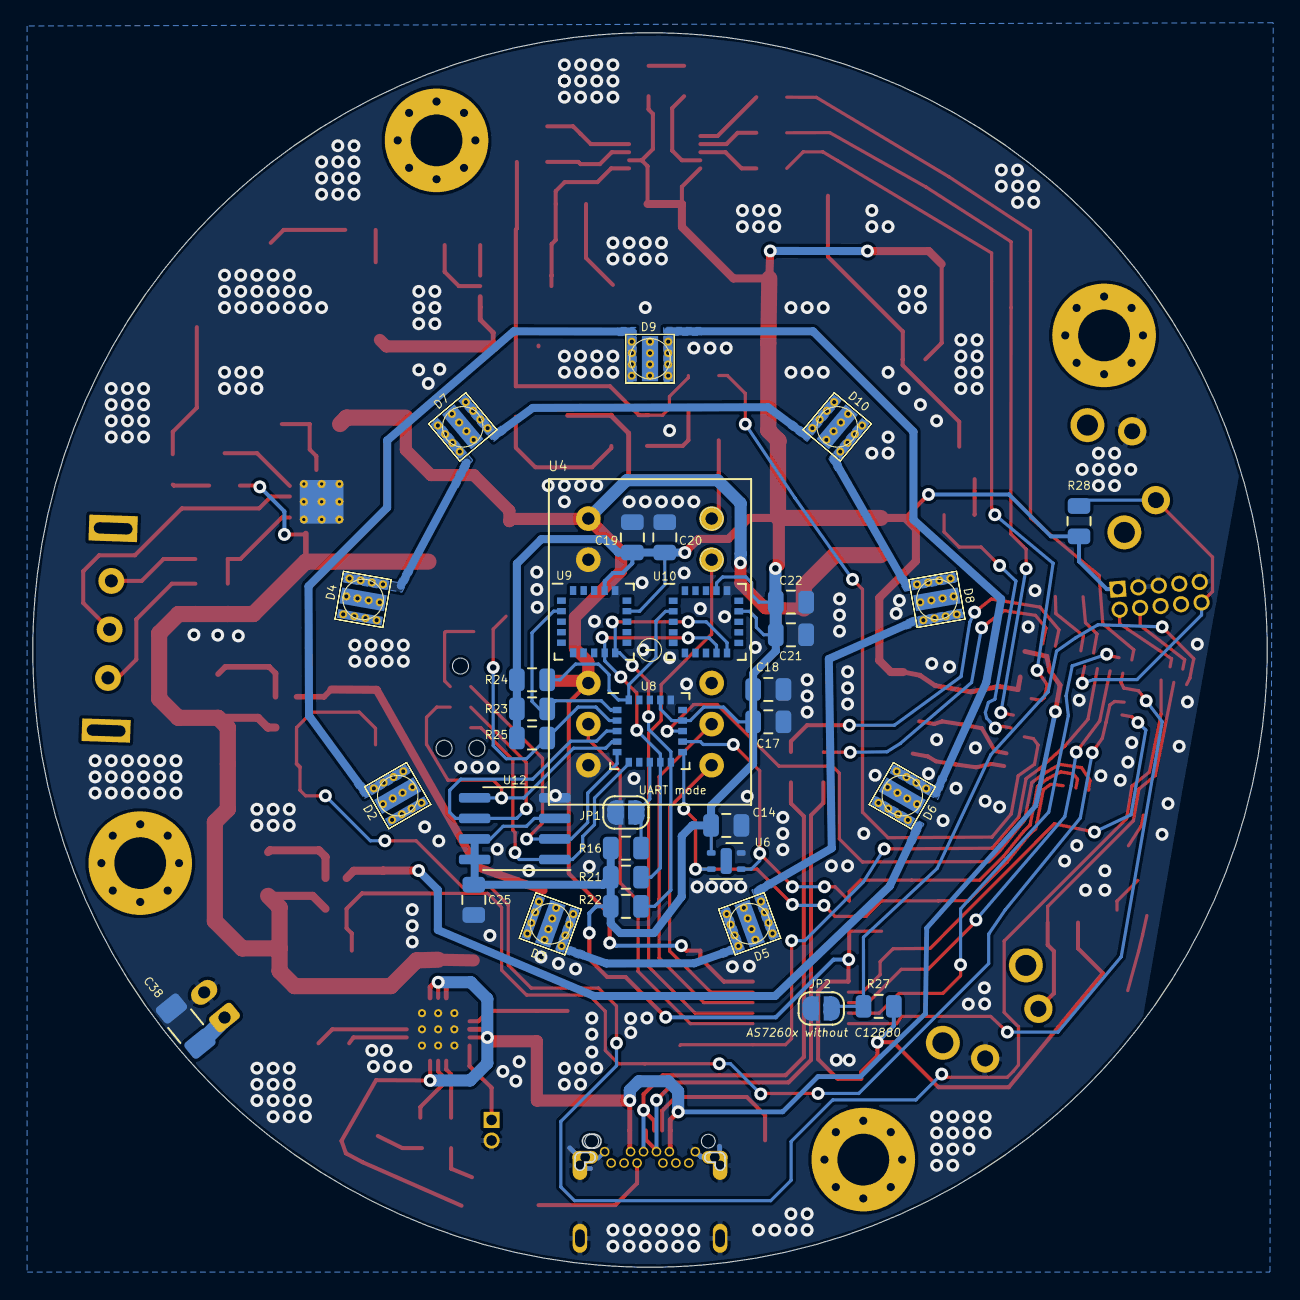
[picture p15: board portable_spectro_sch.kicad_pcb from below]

Board: 2 copper layers, 76.3 x 76.3 mm, 161 parts (34 on the bottom side), 102 nets.
